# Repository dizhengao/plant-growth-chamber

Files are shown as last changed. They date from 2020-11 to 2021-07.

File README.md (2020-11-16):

# Plant Growth Chamber
[Link](https://www.hackster.io/biomaker-2019-team-8/ctod-from-cells-to-droplets-2b3b4f 'this is not yet the link to plant-chamber project') to hackster to be added here.
## Overview and Perspective
This project aims at building an automated plant growth chamber to grow and monitor *Arabidopsis thaliana* seedlings for plant research. The chamber will be equipped with following the features:

1. Provide a humidity, light and temperature-controlled environment which reach to **research level** - meaning that we aim at implementing it in real plant research and experiments conducted in given growth conditions are reproducible. 
2. **Real-time monitoring** of plant growth (camera +  humidity, light and temperature data) though Arduino WiFi module or Raspberry Pi.
3. Pumps for **auto-irrigation**. 
4. A **robotic arm** that can be used to perform some manual control remotely.
6. **Expandable** to larger scale and allow customable purposes. 
5. [Hopefully we can also develop a method to sow small *Arabidopsis* seeds automatically (maybe start with tobacco seeds which are larger!)]

The project will be based on 3D printing, Arduino (maybe together with Raspberry Pi), robotic arm and more.

### Motivation
*Arabidopsis thaliana* is model plant species widely used in plant research. The labor that has been put into growing and taking caring of those plants by researchers all over the world is unimaginable. We propose that simple automation designs could greatly speed up this processes and save researchers' time. [How automation can help xxx]

>TODO: High-throughput screening of many arabidopsis on a plate. 

>TODO: Generalization to other purposes and other plant species.

### Previous designs
>TODO: Search previous designs on hackster websties and others 

### More ideas
Please check our Design folder to find out how our ideas develop and some interesting designs.

## Start
Idea started in mid 2020. Documentation started on 12.11.2020.
Real project has not started but will be soon (hopefully...).
## Folder Index
1. 3D: Files for the 3D printing parts.
2. Code: .ino files for Arduino.
3. Design: Ideas and graphs.
4. Application: application files for Biomaker challenge 2020 (this should not be included in the final github page).

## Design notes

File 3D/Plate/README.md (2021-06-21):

3D print files for the 24-well plates and components of container.

List of items:

1. 24-well-plate: the plate for growing Arabidopsis seedlings
2. Tamp: a tamp to press soil
3. Container: the container for sealing the plate for CF imaging
4. Door: the door of the container for easily moving plates. Together with a bar.

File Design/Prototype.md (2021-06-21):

# Prototype

This file is a general design of the chamber.

- [Prototype](#prototype)
  - [1. Overview](#1-overview)
  - [2. Chamber](#2-chamber)
    - [2.1. Dimensions (cm)](#21-dimensions-cm)
    - [2.2. Growth Conditions](#22-growth-conditions)
    - [2.3. Sensor placement](#23-sensor-placement)
  - [3. Sensors](#3-sensors)
    - [3.1. Temperature-humidity Sensor](#31-temperature-humidity-sensor)
      - [3.1.1. Seeed Temperature, humidity, pressure, gas sensor](#311-seeed-temperature-humidity-pressure-gas-sensor)
      - [3.1.2. Temperature-only sensor](#312-temperature-only-sensor)
    - [3.2. Light Sensor](#32-light-sensor)
    - [3.3. Data collection](#33-data-collection)
    - [3.4. LCD display](#34-lcd-display)
    - [3.5. Camera](#35-camera)
  - [4. Control](#4-control)
    - [4.1. Temperature control](#41-temperature-control)
    - [4.2. Light](#42-light)
  - [5. Data logging and visualisation](#5-data-logging-and-visualisation)

## 1. Overview

1. Box (box + plate for plants + lamp + fan + mount)
2. sensor (circut + data log)
3. Enviortnment Control (Temp + Light + humidity + irrigation).
4. WiFi module
5. Cloud (website (heroku or github page or something)) and visulasition  
6. Robotic arm
7. [Thermal cameras](http://plantphenotyping.com/products/plantscreen-imaging-sensors/#fluorcam)
8. [Fluorescence cameras](http://plantphenotyping.com/products/plantscreen-imaging-sensors/#fluorcam) for in-box CF imaging.

## 2. Chamber

### 2.1. Dimensions (cm)

| Plant growing board    | Arduino board        | Raspberry Pi          | 4D touch screen | Raspberry Pi Screen |
| ---------------------- | -------------------- | --------------------- | --------------- | ------------------- |
| $12\times7.3\times1.8$ | $16\times7.5\times3$ | $8.5\times5.5\times2$ | $9\times5$      |                     |

### 2.2. Growth Conditions

Temperature: 20-22oC  
Humidity: 60%  
Light intensity: 6000 Lum or 150-200 PPFD (Photosynthetic Photon Flux Density).  

### 2.3. Sensor placement

Light sensor: near the growing board facing upward
Temperature sensor: on the wall
Humidity sensor: on the wall (how do we tell if the plant needs to be watered)

Camera: on the top of the chamber

Water pump: where to put it???

## 3. Sensors

### 3.1. Temperature-humidity Sensor

#### 3.1.1. Seeed Temperature, humidity, pressure, gas sensor

Check out xxx <mark> (add linke to .ino here).

#### 3.1.2. Temperature-only sensor

| Sensor Type| In XOD Library? | Physics(reading to Temp value)| Data Type |   Data Logging Method|
| ---------- | --------- | -------- | -------- | ----------- |
| NTC thermistors    | NO       |   [Steinhart-Hart equation](https://learn.adafruit.com/thermistor/using-a-thermistor) | Analog     | TBD|

| Sensor Type| In XOD Library? | Physics(reading to Temp value)| Data Type |   Data Logging Method|
| ---------- | --------- | -------- | -------- | ----------- |
| LM75   | Yes (download library from bio-maker tutorial)       |   Read directly through I2C bus | Digital | TBD|

The two sensors agree with each other

### 3.2. Light Sensor

| Sensor Type| In XOD Library? | Physics(reading to Temp value)| Data Type |   Data Logging Method|
| ---------- | --------- | -------- | -------- | ----------- |
|GL5528 photoresistor| NO      |  TBD  | Analog | TBD|

Analog sensor of low quality. Only roughly tells if the lights are bright enough. Can not be used for precise measurement.

### 3.3. Data collection

Check out ThingSpeak(https://thingspeak.com) and some examples (https://community.thingspeak.com/tag/raspberry-pi/)
Not accurate and can not tell humidity. 

### 3.4. LCD display

Address should be 20h (or 0x20), the document provided by the biomarker website is wrong.

### 3.5. Camera

See full instruction on how to set up [Raspberry pi camera](../Code/Camera/instruction-PiCamera.md) or [webcam](../Code/Camera/instruction-Webcam.md) through USB. Live stream can be viewed on adafruit IO's [feed](https://io.adafruit.com/Deebug/feeds/pi-camera) page.

## 4. Control

### 4.1. Temperature control

Large polystyrene box +
[Heating elements](https://uk.rs-online.com/web/p/heating-elements/2995950/), [air circulation Fan](https://uk.rs-online.com/web/p/axial-fans/6688827/), [cooling fan](https://www.banggood.com/Geekcreit-12V-6A-DIY-Electronic-Semiconductor-Refrigerator-Radiator-Cooling-Equipment-p-1074404.html?akmClientCountry=CN&cur_warehouse=CN), insulation panel

### 4.2. Light

LED panels from Photon (Czech):
- [LED Fyto-Panels from Photon](http://led-growing-lights.com/products/led-fyto-panels/#downloads) - Very expensive
- [Compact LED Bars](http://led-growing-lights.com/products/led-bars/compact-led-bars/#details)- Very expensive. 
  - PPFD: max. 920 µmol.m-2.s-1 (at the distance of 50 cm)
  - Light source: 12 x 126 pcs. LED 5,700 K cool white
  - Compact LED Bars ( stand-alone system with standard powering option) 2,690 €
- [LED Lights SL 3500](http://led-growing-lights.com/products/led-lights-sl-3500/): The one used in Wanne's lab.
  - 20x20 cm RGB. Light emitting diodes (LEDs): 455 nm, 530 nm, 617 nm, cool white (4,500 - 10,000 K) and others
  -  High light output - up to 3,000 µmol.m-2.s-1 at the distance of 20 cm
  - £4,500 with a controller

## 5. Data logging and visualisation

Connect Arduino to Rpi, and use Rpi to upload data to a Adafruit-IO or use Heroku.

Also display on a LCD screen.

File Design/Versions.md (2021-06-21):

# Versions

This file is a summary of different chamber versions.

## Version 1

### Time

Apr - Jun 2021

### Features

1. Temperature, humidity and pressure data logged to Adafruit (real-time monitoring) and Google drive (long-term storage and data analysis)
2. Low-resolution images taken every 30s for Adafruit (real-time monitoring) and high-resolution images taken every 30min for Google drive (long-term storage and data analysis)
3. Auto-irrigation every 48 h (Changed to 60 h later)

A 14-day trial was done from 27.4.21 to 10.5.21. Refer to [Trials](../Trials/Trials.md) for more information.

### Images

Refer to Pictures/Box/Version1 and Pictures/Circuit/Version1

## Version 2

### Time

17th Jun - xxx 

### Expectation

0. [x] Clean layout.
1. Temperature and humidity control.
2. Sufficient (and adjustable) light source.
3. Programmable light switch.

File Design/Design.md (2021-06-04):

# Design

This file summaries general design ideas and resources to build the project.

- [Design](#design)
  - [1. Ideas](#1-ideas)
  - [2. Questions](#2-questions)
  - [3. Reference](#3-reference)
    - [3.1. General](#31-general)
    - [3.2. Suppliers](#32-suppliers)
    - [3.3. Some Hackster projects](#33-some-hackster-projects)
    - [3.4. Hardware](#34-hardware)
      - [3.4.1. Relay](#341-relay)
      - [3.4.2. WiFi](#342-wifi)
      - [3.4.3. 4D Systems programmable touchscreen](#343-4d-systems-programmable-touchscreen)
    - [3.5. Software-Arduino IDE](#35-software-arduino-ide)
    - [3.6. Software-3D printing](#36-software-3d-printing)
    - [3.7. Software-XOD](#37-software-xod)
      - [3.7.1. XOD libraries for Open-Smart Rich UNO R3](#371-xod-libraries-for-open-smart-rich-uno-r3)
      - [3.7.2. Basic XOD elements](#372-basic-xod-elements)
    - [3.8. Other references](#38-other-references)
    - [3.9. Arduino-Rpi communication](#39-arduino-rpi-communication)
    - [3.10. Raspberry pi](#310-raspberry-pi)
  - [4. Knowledge](#4-knowledge)
    - [4.1. Electrical Sensors](#41-electrical-sensors)
    - [4.2. WiFi modules](#42-wifi-modules)
    - [4.3. Programming on Hardware](#43-programming-on-hardware)
    - [4.4. DIY](#44-diy)
  - [5. Papers](#5-papers)

## 1. Ideas

quick thoughts can be added here

[20210420-JMH] 1. To test watering system, fill plates with soil and see the change of soil color from camera. 2. Firmly press the soil by printing a 'presser' with the same dimensions as plates. 3. Whether use compost only or with vermiculite.

[20200303-ZD] Thermo cameras and fluorescence cameras. Also check out devices on [Photon](https://handheld.psi.cz/).

[20201203-ZD] To have another raspberry Pi with screen showing real time images and data logs, which can be put in home/lab bench so that you won't even have to have a computer to do the monitoring. It would be great if we have this along side with our prototype at the showcase event.

[20201125-Che] Lamp: Control RGB light separately; create different light intensity and RGB components for different experimental purposes.

[20201123-JMH] 1. Use robotic arm or something else to spray water from the top. This will be especially useful to water individual wells that are dried as a complement of watering from the bottom. 2. May include lime as CO2 scrubber to customize CO2 concentration for experiment purposes.

[20201115-ZD] Expand the prototype to larger scale: Use a robot with a camera to move around and take pictures of plants every xx minutes/hours; or install tracks for camera on the top of the chamber to take images every xx minute/hour.

## 2. Questions

*Mar 21*

1. [x] How to connect Arduino to Rpi, and use Rpi to upload data to a cloud?

*Feb 21 - sadly we no longer use XOD*

1. [x] How to search XOD nodes? 
2. [x] How to create our own nodes? And how hard/easy is this?
3. [x] Devices using I2C protocol- How to find out their address? Does each of device come with different address or we can customize the address?
4. [x] What is DONE used for on XOD?

## 3. Reference

### 3.1. General

[Letusgrow](https://www.lettusgrow.com)  
[Growcab](https://wikifactory.com/+growcab/growcab)

### 3.2. Suppliers

- [RS](https://uk.rs-online.com/web/)
- https://thepihut.com/
- https://shop.sb-components.co.uk/collections/raspberry-pi
- https://shop.pimoroni.com/
- https://www.okdo.com/
- https://uk.farnell.com/?pf_custSiteRedirect=true
- https://www.thorlabs.com/

### 3.3. Some Hackster projects

- :star:[FytoScope Chamber FS 130](http://growth-chambers.com/products/small-fytoscopes/fytoscope-chamber-130/#details) from Photon
- [Biomaker Tutorial](https://www.hackster.io/159756/biomaker-tutorial-1-getting-started-4fc966)
- :star:[Lunaflow](https://www.hackster.io/lunaflow/lunaflow-bioluminescent-plankton-for-3d-flow-visualisation-d60cbe): incubator design, **temperature control**, real-time monitor camera, codes.
- [Variable-Time Camera for Monitoring Plant Pollination Events](https://www.hackster.io/team-ppi/variable-time-camera-for-monitoring-plant-pollination-events-ad21e7) A **video and time-lapse monitor** to record pollinators interacting with plants. This project included an environmental sensor to measure temperature, humidity and barometric pressure and wrote this data into the image file names for later analysis.
- [Biofab Incubator](https://www.hackster.io/170194/biofab-incubator-6f5b0e) A low cost programmable incubator for growing mycelium textile. This project uses sensors to measure temperature and humidity and feeds this information back into the system to maintain constant environmental conditions.- [eCO-SENSE](https://www.hackster.io/glen-chua/eco-sense-soil-sensors-powered-by-plant-photosynthesis-be80a2) A sensor to monitor soil conditions powered by plant growth. This project uses a temperature sensor, moisture sensor and gas sensor to take measurements of soil 68 conditions and adds a bluetooth module to send the data wirelessly to a phone or computer.
- [Low Cost Oxygen Sensor for Bioreactors](https://www.hackster.io/biomaker/low-cost-oxygen-sensor-for-bioreactors-c7e066) This project developed a custom low-cost oxygen sensor to measure oxygen levels in cultures of E. coli, and logged the data via an Arduino microcontroller. 
- [A Behavioural Chamber to Evaluate Rodent Forelimb Grasping](https://www.hackster.io/alejandrocarn/a-behavioural-chamber-to-evaluate-rodent-forelimb-grasping-bedb1a) This project uses a light emitter and light sensor to monitor when a rodent moves past a certain threshold, and triggers release of a sugar pellet when it does. 

Refer to some plant growth products and facility that have been using in real plant research (e.g. in PGF) and [gardin](https://gard.in/) (This is very expensive so probably we won't use them in our project.)

### 3.4. Hardware

#### 3.4.1. Relay

- [Connecting a 12v 8 Channel Relay to an External Power Supply and RaspberryPi](https://medium.com/@jinky32/connecting-a-12v-8-channel-relay-to-an-external-power-supply-and-raspberrypi-6fec119c112c)  
- [Control High Voltage Devices with Arduino](https://howtomechatronics.com/tutorials/arduino/control-high-voltage-devices-arduino-relay-tutorial/)

#### 3.4.2. WiFi

Arduino there are some modules based on the [ESP8266 microchip](https://en.wikipedia.org/wiki/ESP8266) such as Adafruit Feather HUZZAH (I have this!, read manual [here](https://learn.adafruit.com/adafruit-feather-huzzah-esp8266)) or [SparkFun ESP8266 Thing Dev Board](learn.sparkfun.com/tutorials/esp8266-thing-development-board-hookup-guide).

#### 3.4.3. 4D Systems programmable touchscreen

[spec sheet](https://static1.squarespace.com/static/584d41b3f5e2310b396cd953/t/5ba376490e2e7299a6f96506/1537439314392/gen4-uLCD-32D_datasheet_R_1_5.pdf), [Introduction](https://static1.squarespace.com/static/584d41b3f5e2310b396cd953/t/5ba374cac2241b80e970e46f/1537438935415/Visi-Genie_userguide_R_2_0.pdf)

### 3.5. Software-Arduino IDE

Add resources here.

### 3.6. Software-3D printing

Add resources here.

### 3.7. Software-XOD

#### 3.7.1. XOD libraries for Open-Smart Rich UNO R3

- Real time clock module: datetime (https://xod.io/libs/xod/datetime/) and ds-rtc (https://xod.io/libs/xod- dev/ds-rtc/) libraries.
- Onboard LM75 temperature sensor: lm75a-temp-sensor node can be found in the gst/lm75atempsensor XOD library.
- Onboard 4-digit display: tm1637-dev node from the cesars/tm1637 or cesars/tm1637-v2 library. This library also contains other nodes for onboard display, such as tm1637-decex, tm1637-autorange, tm1637-digits (for string)
- Various onboard modules: cesars/rich-uno-r3, cesars/utils (contains nodes required by the her other libraries)
- sd-log node: from xod/commonhardware library, for saving data into SD card.
- OLED screen: wayland/ssd1306-oled-i2c library. Nodes: ssd1306-oled-i2c-device
- gweimer/utils

#### 3.7.2. Basic XOD elements

- Format number: *format-number* node
- *join* node

### 3.8. Other references

- [Robotic arm](https://shop.pimoroni.com/products/mearm-robot-raspberry-pi-kit?variant=21775370223699&currency=GBP&utm_source=google&utm_medium=cpc&utm_campaign=google+shopping?utm_source=google&utm_medium=surfaces&utm_campaign=shopping&gclid=Cj0KCQiA48j9BRC-ARIsAMQu3WTvhcmb-bZv5fxLHJMAYPL-1Bl-ShvdAIO8ML_nc9I4GpWhqUfcmDkaAn6uEALw_wcB), [Makeblock robot](https://www.makeblock.com/cn/mbot/)
- https://www.nature.com/articles/d41586-019-01590-z
- [Open-source lab](https://www.appropedia.org/Open-source_Lab)
- [BENEFICIAL BIO](https://beneficial.bio/)
- [Photon-plant phenotyping systems](http://plantphenotyping.com/)

### 3.9. Arduino-Rpi communication

An introduction [article](https://roboticsbackend.com/raspberry-pi-arduino-serial-communication/).

Python packages: [pySerial API](https://pyserial.readthedocs.io/en/latest/pyserial_api.html)

On Arduino side: [UART](https://www.arduino.cc/reference/en/language/functions/communication/serial/)

### 3.10. Raspberry pi

- [Pi Camera](https://projects.raspberrypi.org/en/projects/getting-started-with-picamera/4) control with Python.
- Live stream with [USB webcam on local browser](https://tutorials-raspberrypi.com/raspberry-pi-security-camera-livestream-setup/) or with [pi-camera](https://learn.adafruit.com/cloud-cam-connected-raspberry-pi-security-camera/adafruit-io), [pi-camera using motion](https://learn.adafruit.com/cloud-cam-connected-raspberry-pi-security-camera?view=all). Also see this for a wayaround 
- [rsync](https://www.raspberrypi.org/documentation/remote-access/ssh/rsync.md)
- [Servo moter](https://learn.adafruit.com/adafruits-raspberry-pi-lesson-8-using-a-servo-motor)
- [Power Control](https://learn.adafruit.com/adafruits-raspberry-pi-lesson-13-power-control)

## 4. Knowledge

### 4.1. Electrical Sensors

Che wrote:

- How do we communicate with sensors? clock
- How we process the data reading from sensors?
- Data log and plots.
- Initializing and calibration. [ZD] Temp: using a thermometer; Light intensity: ZD can borrow a professional one from lab; humidity: buy a professional one from Amazon?
- Camera-> [ZD] There are many camera modules for Raspberry Pi but not as many for Arduino (as far as I know...). So (1) use Raspberry Pi (2) search for more Arduino projects with camera; (3) search for adapters to connect Arduino and Raspberry Pi cameras.

### 4.2. WiFi modules

Che wrote:

- How do we achieve remote control and communication through WiFi? ->[ZD] For Raspberry Pi it is very straightforward as it has built-in WiFi module, for Arduino there are some modules based on the [ESP8266 microchip](https://en.wikipedia.org/wiki/ESP8266) such as Adafruit Feather HUZZAH (I have this!, read manual [here](https://learn.adafruit.com/adafruit-feather-huzzah-esp8266)) or [SparkFun ESP8266 Thing Dev Board](learn.sparkfun.com/tutorials/esp8266-thing-development-board-hookup-guide).

### 4.3. Programming on Hardware

Che wrote:

- Syntax of the programming language;
- Debug and tests scheme.
- Development tools.

### 4.4. DIY

ZD:

- chamber (Should have enough insulation for heat)
- plates for growing Arabidopsis
- scaffolds to mount sensors

Che wrote:

- 3D printing and CAD models.
- Robotic arms

## 5. Papers

1. Jolles, J. Broad-scale Applications of the Raspberry Pi: A Review and Guide for Biologists. https://ecoevorxiv.org/qh9sz/ (2021) doi:10.32942/osf.io/qh9sz.
1. Tausen, M. et al. Greenotyper: Image-Based Plant Phenotyping Using Distributed Computing and Deep Learning. Front. Plant Sci. 11, (2020).
1. Gaggion, N. et al. ChronoRoot: High-throughput phenotyping by deep segmentation networks reveals novel temporal parameters of plant root system architecture. bioRxiv 2020.10.27.350553 (2020) doi:10.1101/2020.10.27.350553.

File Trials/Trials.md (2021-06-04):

Trials/27.4# Trials

## 1st trial: 27.4.21-10.5.21

### Summary

This is our first trial aiming to test some basic features before moving forward, starting from 11am 27.4.21 and lasted for 14 days. This is the first version of box and 24-well plate, with no environment controls and low brightness light. 1 Pai choi seed was sown per well.

#### Features

1. Temperature, humidity, pressure data were pushed to Adafruit-IO every 30s for real-time monitoring and saved to Google drive for long-term storage.
2. Low-resolution images were taken every 30s and pushed to Adafruit for real-time monitoring. High-resolution images were taken every 30min and saved to Google drive for long-term storage and data analysis.
3. Auto-irrigation every 48 h (Changed to 60 h later).

#### Problems

0. Error logs can be found in the working directory. Some general problems are summaries below.
1. Program was interrupted many times because of Internet connection failure. -> Separate local data logging and data upload into two parallel program will solve this.
4. Temperature in the chamber is high when light is on (Compare NTC values and LM75 values). -> Temperature control features will take care of this.
5. Humidity in the chamber is low when light is on. -> Humidity control features will take care of this.
6. Too much water during auto-irrigation, and water cannot drain away. Changed irrigation intervals to 60h. Need to reduce watering time from 30s to 15s (or 10s) next time. -> Irrigation calibration will take care of this.
7. Light intensity was not enough.

Some error logs

2. 2021/04/28 11:33:04AM: Sensors data interrupted (unknown reasons...) but images were taken and uploaded as normal. Restarted Rpi and re-located the box to kitchen at 22.15.
3. 2021/04/30 12pm: Sensors data interrupted (unknown reasons...) but images were taken and uploaded as normal. Restarted Rpi.

### Improvement and upcoming features

1. Separate local data logging process and data upload process into two parallel program will be able to disentangle local data logging from any Internet connection problems, ensuring that data is not lost when Internet is down.
2. Temperature and humidity control features will be implemented in the next version.
3. Calibrate irrigation intervals, duration and make a hole at the bottom of the container to drain redundant water.
4. Use a brighter light source.

### Images

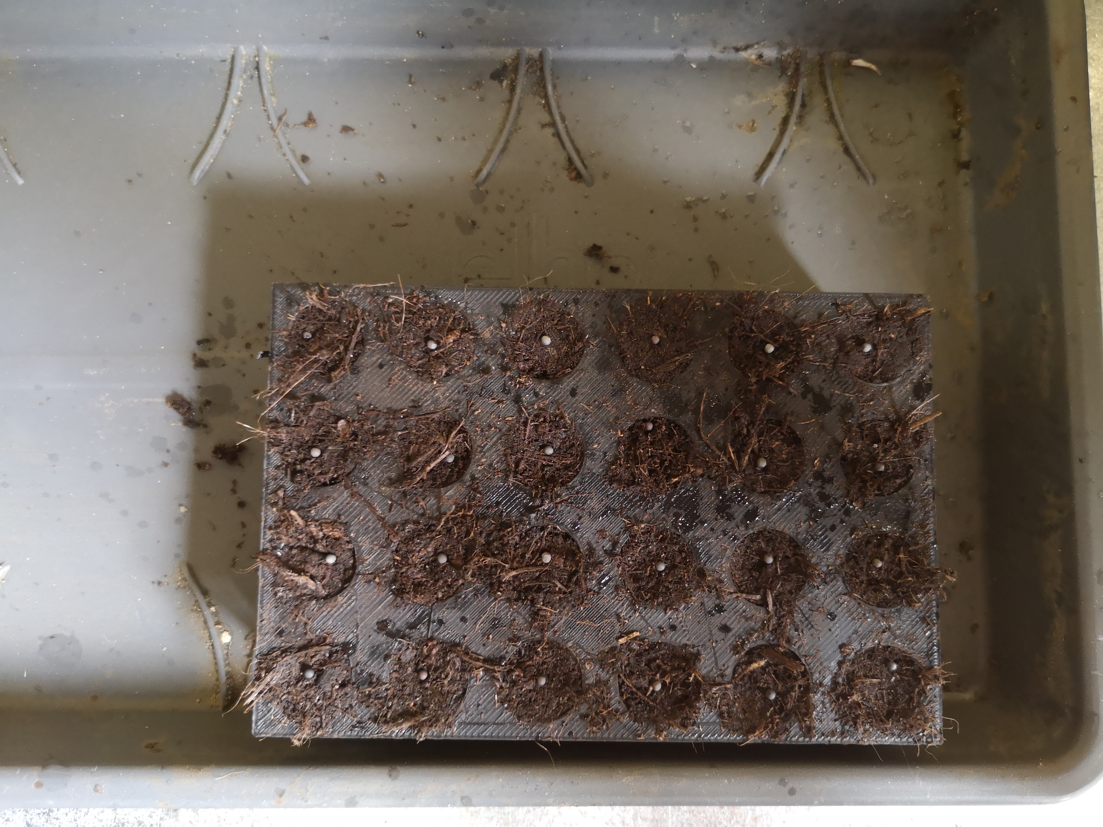
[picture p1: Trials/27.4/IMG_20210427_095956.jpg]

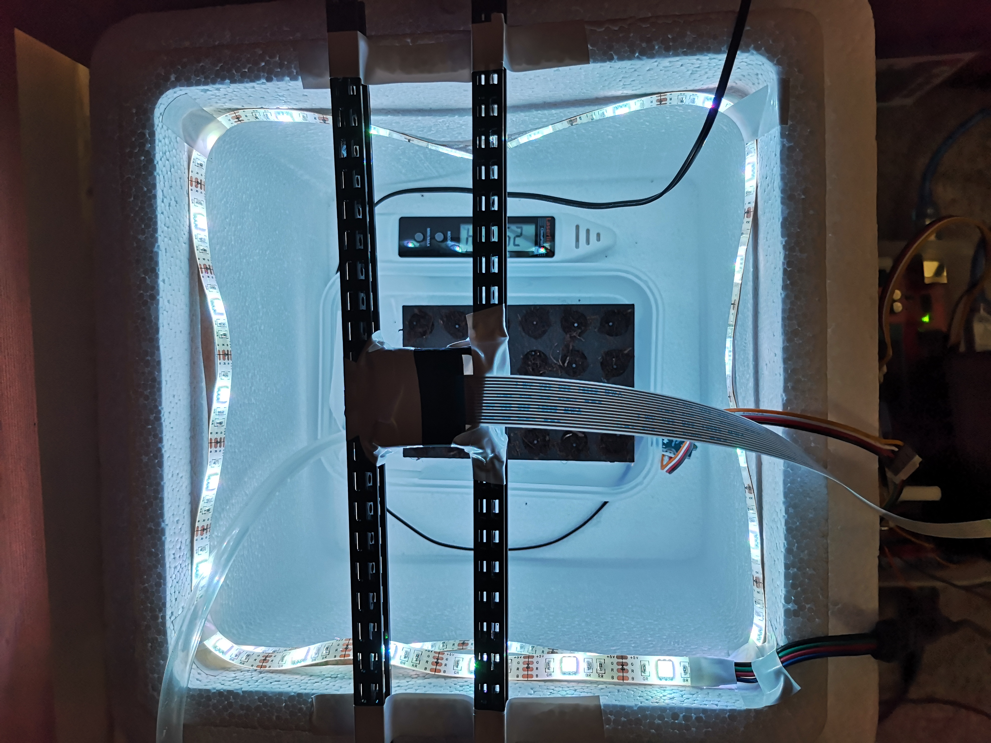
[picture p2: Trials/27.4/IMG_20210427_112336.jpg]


### Results

Environmental data during the 14-day trial is shown below. The environment will be more controlled in our next version.
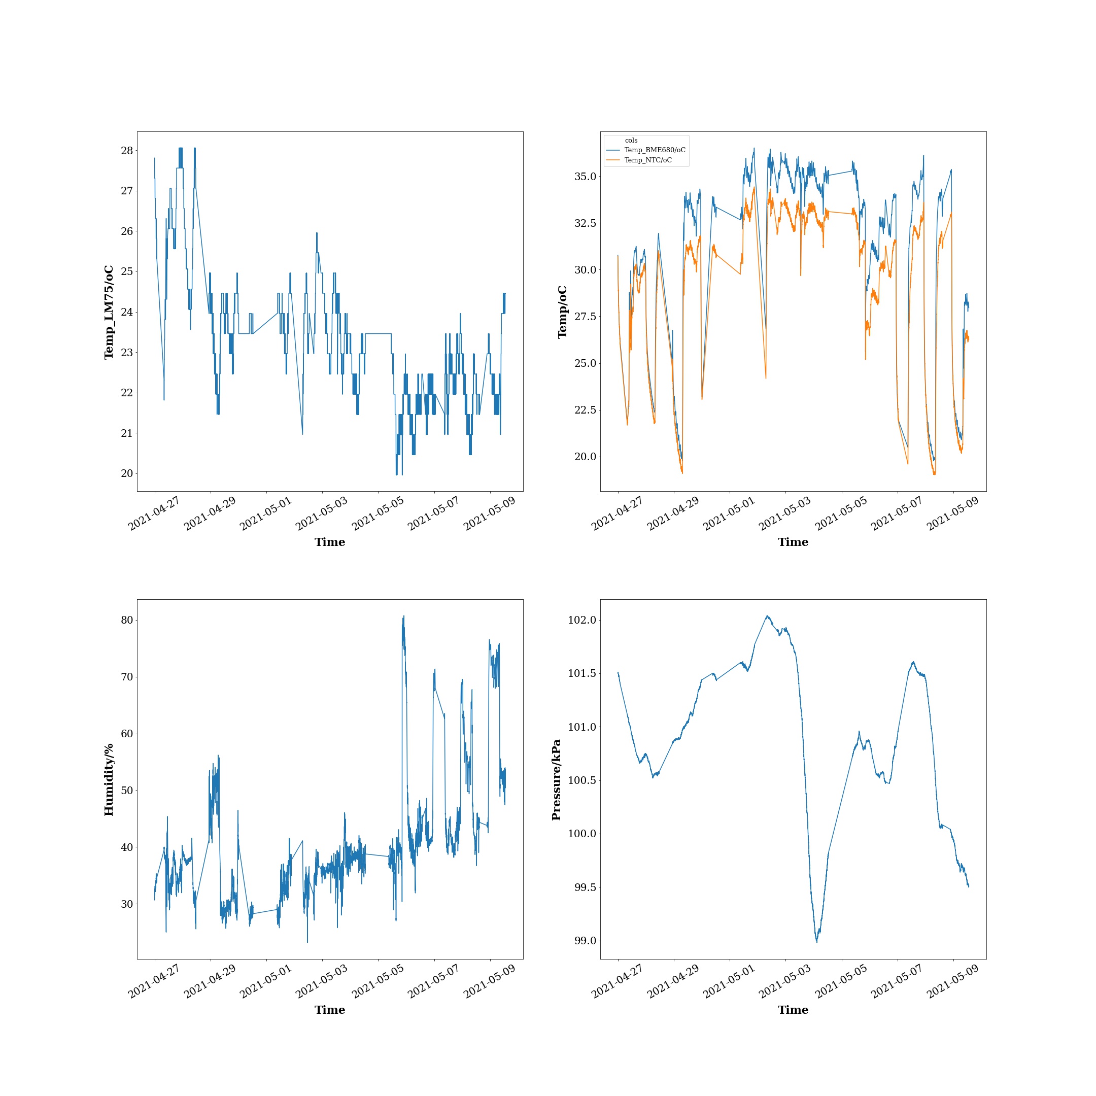
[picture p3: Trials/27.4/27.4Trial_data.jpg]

>Plot legend: Temperature, humidity and pressure data during the first trial. Top left: Temperature outside of the box. Top right: Temperature within the box measured by two different sensors. Bottom left: Relative humidity within the box. Bottom right: Air pressure within the box.

A [time-lapse video ](https://youtu.be/F5084XwlkN0) was made from high-resolution images taken by Raspberry Pi.

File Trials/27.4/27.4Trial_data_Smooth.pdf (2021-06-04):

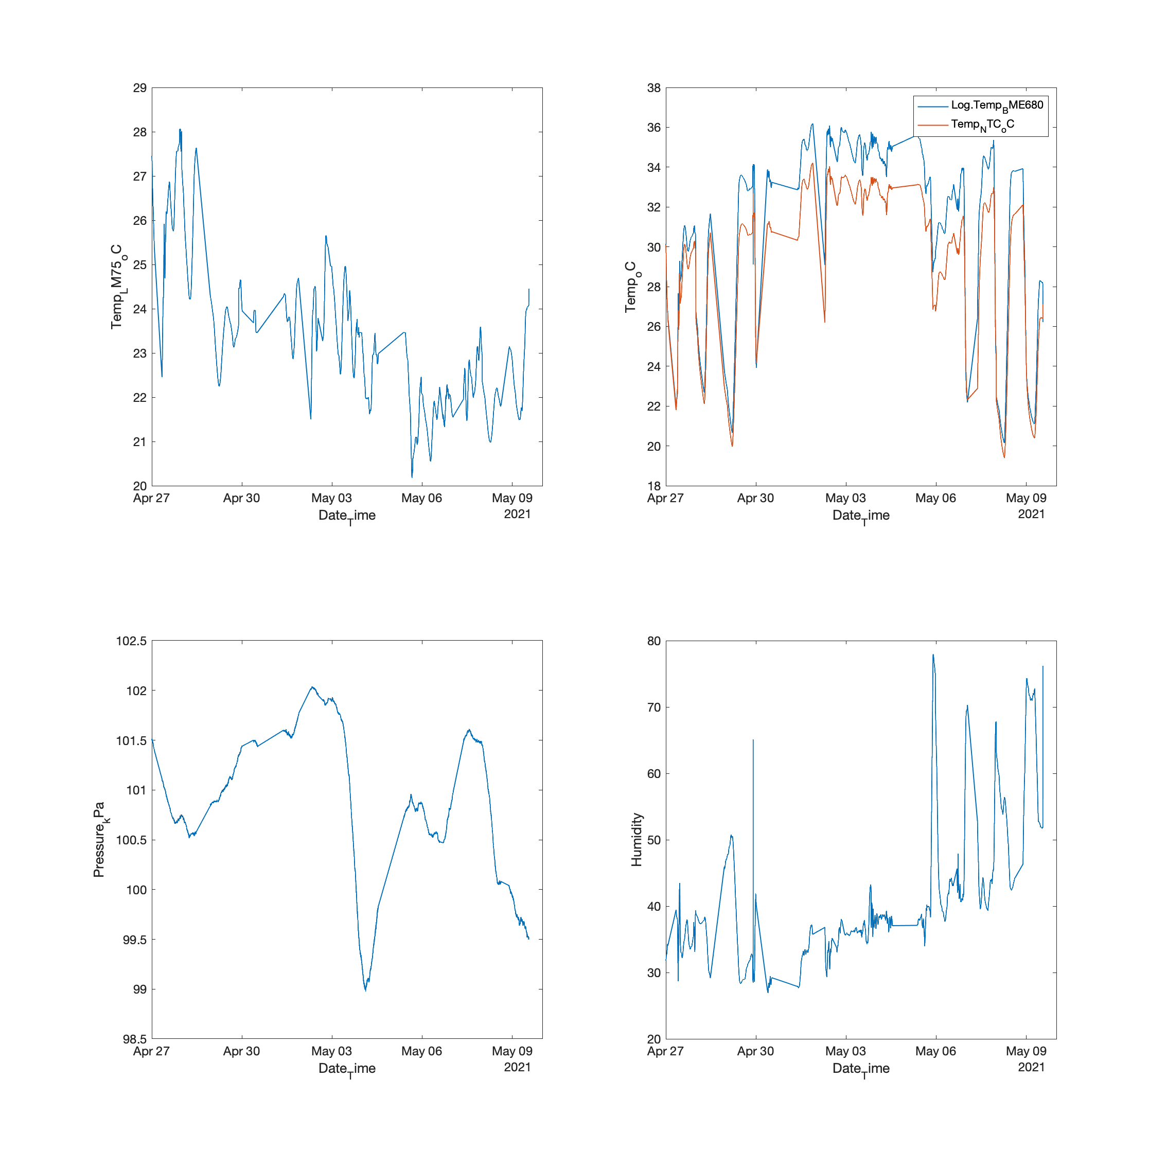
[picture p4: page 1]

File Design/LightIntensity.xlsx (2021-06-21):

Distance/cm | PPFD | Notes
10 | 3000 | Full Beam. Measured on 12.6.21 by LI6800. The light was held by hand so these are just rough numbers
15 | 1700
20 | 1100
25 | 700
30 | 550

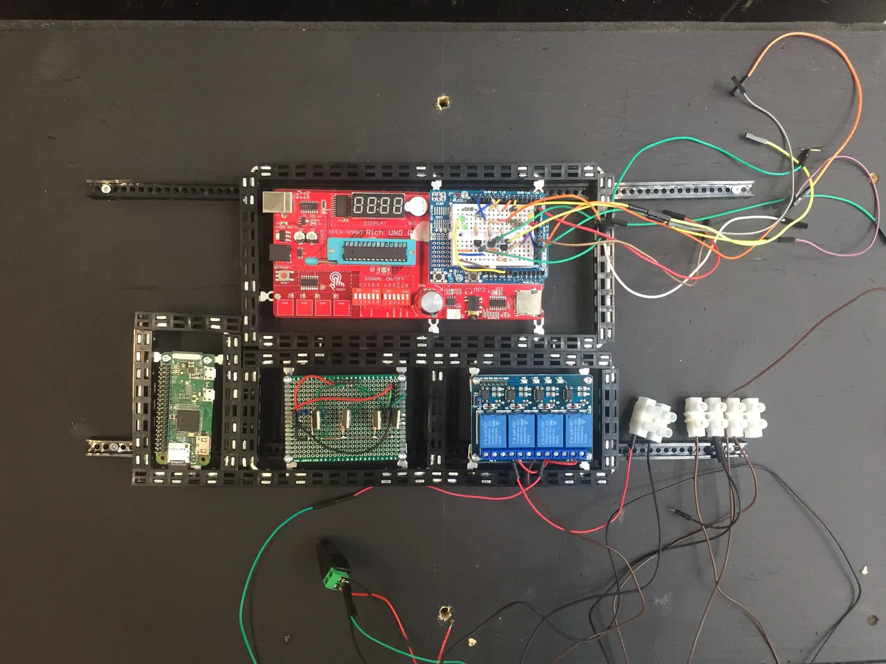
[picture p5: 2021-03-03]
Pictures/ref-mounted-electronics.jpg

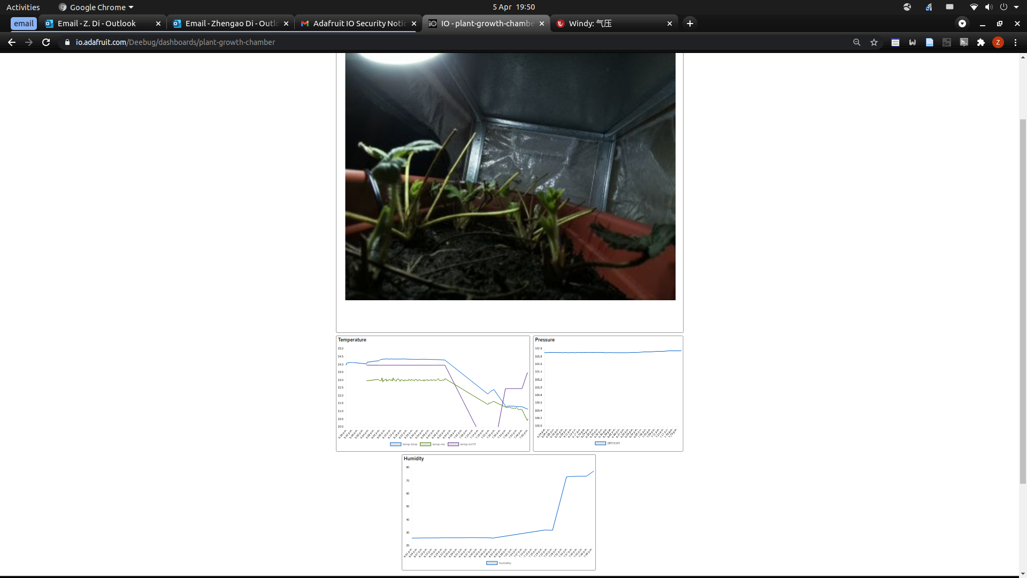
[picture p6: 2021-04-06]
Pictures/Screenshot from 2021-04-05 19-50-20.png

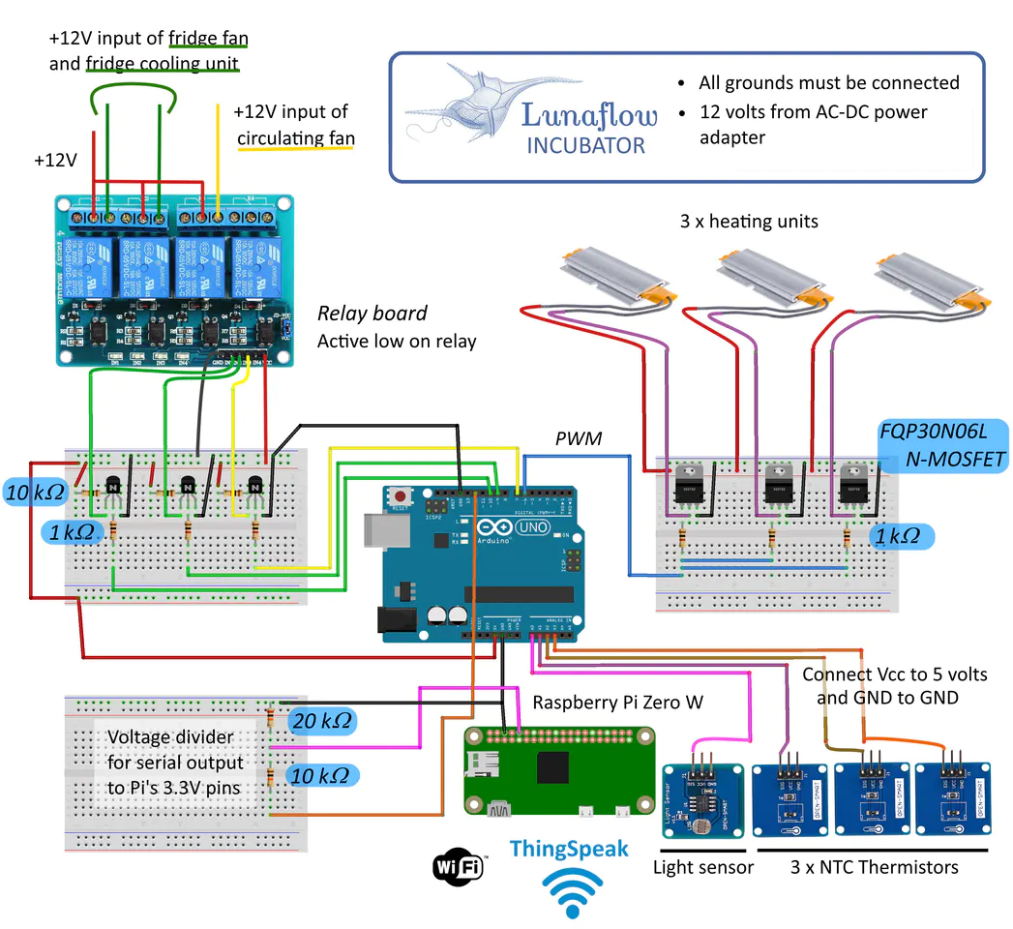
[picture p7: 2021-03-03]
Pictures/Ref-incubator-circuit.jpg

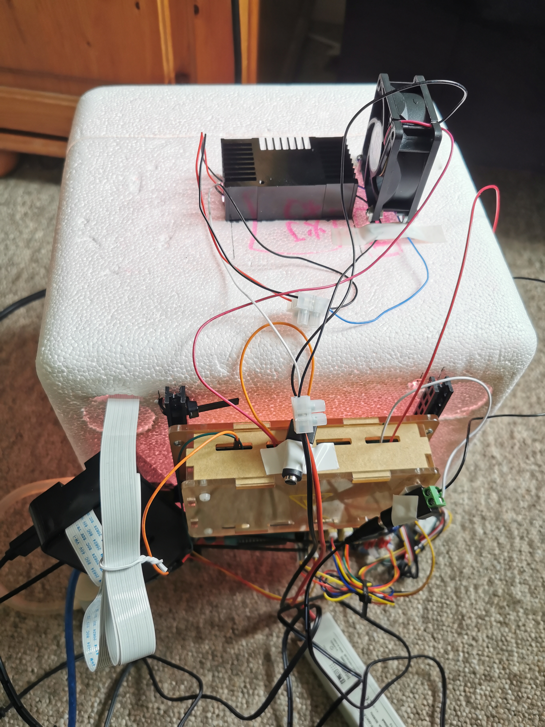
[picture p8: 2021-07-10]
Pictures/Box/Version2/Box2.0(Back_new).jpeg

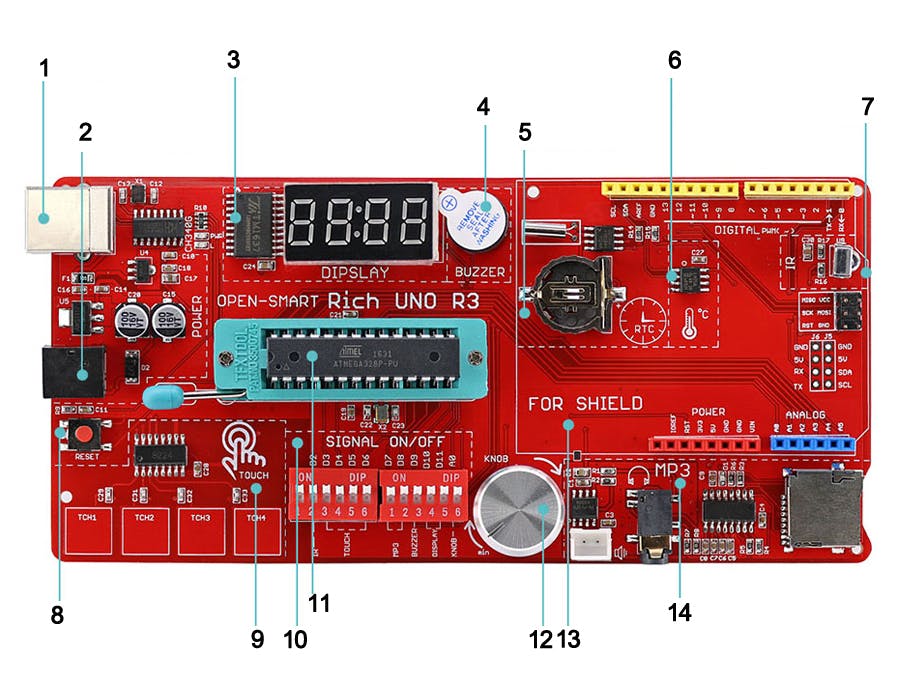
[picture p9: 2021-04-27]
Pictures/Rich UNO R3 multifunction board.jpg

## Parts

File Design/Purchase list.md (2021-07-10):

# Shopping list

- [Shopping list](#shopping-list)
  - [1. Ideas](#1-ideas)
  - [2. 已购](#2-已购)
  - [3. To Buy](#3-to-buy)
  - [- [ ] Cooler?](#----cooler)
  - [Light](#light)
  - [Supplier](#supplier)

Code PDGU.EZZZ

## 1. Ideas

- [Jumper Wire](https://uk.rs-online.com/web/p/breadboard-jumper-wire/5053396/)
- [Light](https://uk.rs-online.com/web/p/led-strip-lights/9125016/): Need 6000 lumens. Check out [LED Kits](https://uk.rs-online.com/web/c/displays-optoelectronics/led-lighting-system-components/led-kits/?sort-by=Application&sort-order=desc&pn=1) from RS
- An all-in-one sensor [Enviro](https://shop.pimoroni.com/products/enviro?variant=31155658489939)
- Lamp: [Ali](https://www.aliexpress.com/item/4001095381063.html), [Rpi](https://tutorials-raspberrypi.com/connect-control-raspberry-pi-ws2812-rgb-led-strips/), [PPF and Lumen](https://www.waveformlighting.com/horticulture/convert-ppf-to-lumens-online-calculator)
- [Fan](https://thepihut.com/products/miniature-5v-cooling-fan-for-raspberry-pi-and-other-computers?_pos=2&_sid=7ba767831&_ss=r)
- [Water Pump](https://thepihut.com/products/peristaltic-liquid-pump-with-silicone-tubing-5v-to-6v-dc-power?_pos=5&_sid=7ba767831&_ss=r), https://uk.rs-online.com/web/p/water-pumps/9146944/
- IoT kit https://www.sparkfun.com/products/14682

This webpage contains useful information about integrated sensors for RaspberryPi: [RaspberryPi sensor list and tutorial](https://tutorials-raspberrypi.com/raspberry-pi-sensors-overview-50-important-components/)

## 2. 已购
0. [Pump](https://www.ebay.co.uk/itm/MINI-SUBMERSIBLE-WATER-PUMP-3V-to-6V-DC-AQUARIUM-arduino-UK-seller-BBC-micro/122508463023): DC Voltage:2.5-6V. Maximum lift:40-110cm. Flow rate:80-120L/H
1. **Two** Raspberry Pi 4 B 4GB, RS Stock No. 182-2096, https://uk.rs-online.com/web/p/raspberry-pi/1822096/
2. LCD Touch Screen with 7in Capacitive Touch Screen, RS Stock No. 899-7466, https://uk.rs-online.com/web/p/products/8997466/
3. Two Sandisk Storage Card 16Gb, RS Stock No. 121-3897, https://uk.rs-online.com/web/p/products/1213897/
4. Two Okdo Raspberry Pi Power Supply, USB Type C with Universal Plug Type, 1.5m, RS Stock No. 187-1381, https://uk.rs-online.com/web/p/products/1871381/
5. DesignSpark ABS Case, RS Stock No. 117-6025, https://uk.rs-online.com/web/p/products/1176025/
6. SAD-01, Breadboard Prototyping Board, RS Stock No. 453-8824, https://uk.rs-online.com/web/p/breadboards/4538824/
7. 1.75mm Black PLA 3D Printer Filament, 300g RS Stock No. 832-0406, https://uk.rs-online.com/web/p/3d-printing-materials/8320406/
8.  Raspberry Pi, Camera, RS Stock No. 913-2664, https://uk.rs-online.com/web/p/raspberry-pi-cameras/9132664/
9.  2* [heating element, RS Stock No. 299-5950](https://uk.rs-online.com/web/p/heating-elements/2995950/)
10. [Bostik Bond-Flex 100HMA Black Sealant Non-Slump Paste 300 ml Cartridge. RS Stock No. 341-0955](https://uk.rs-online.com/web/p/sealants/3410955/)
11. 3* [Seeed Studio 101020513, Grove-Temperature, Humidity, Pressure and Gas Sensor (BME680) for BME680 RS Stock No. 184-5086](https://uk.rs-online.com/web/p/sensor-development-tools/1845086/)
12. 2* [Raspberry Pi 1m HDMI to Micro HDMI Cable in Black. RS Stock No. 187-1377](https://uk.rs-online.com/web/p/raspberry-pi-cables/1871377/)
13. [Laserliner 082.034A Digital Hygrometer, RS Stock No. 191-9564](https://uk.rs-online.com/web/p/hygrometers/1919564/)
14. [Okdo ABS Case in Black. RS Stock No. 187-3799](https://uk.rs-online.com/web/p/raspberry-pi-cases/1873799/)
15. [Feather HUZZAH 3213](https://www.mouser.co.uk/ProductDetail/Adafruit/3213/?qs=AQlKX63v8RuWaQY9I2LOXA%3D%3D)
16. [RS PRO 1kΩ Carbon Film Resistor 2W ±5%. RS Stock No. 707-8861](https://uk.rs-online.com/web/p/through-hole-fixed-resistors/7078861/)
17. [RS PRO 10kΩ Carbon Film Resistor 2W ±5%, RS Stock No. 707-8906](https://uk.rs-online.com/web/p/products/7078906/)
18. [12 V dc, DC Axial Fan, 60 x 60 x 25mm, 39.1m³/h, 2.8W. RS Stock No. 668-8827](https://uk.rs-online.com/web/p/axial-fans/6688827/)
19. 3* [Sandisk Storage Card for Raspberry Pi, 16GB NOOBs RS Stock No.:121-3897](https://uk.rs-online.com/web/p/raspberry-pi-os/1213897/) 
20. [Samsung 32 GB MicroSDHC Card Class 10 RS Stock No. 144-9017](https://uk.rs-online.com/web/p/micro-sd-cards/1449017/)
21. [RS PRO 0.8MP 30fps Webcam, 1080 x 720 RS Stock No. 201-3517](https://uk.rs-online.com/web/p/products/2013517/) £66
22. [RS PRO Black Cable Tie Nylon, 300mm x 4.8 mm RS Stock No. 233-487](https://uk.rs-online.com/web/p/products/0233487/) £13.25
23. [Seeed Studio, Grove Base Shield V2 RS Stock No. 174-3233](https://uk.rs-online.com/web/p/products/174-3233/) £6.70
24. 5 * [Seeed Studio 110990210 for use with Grove-Base Shield RS Stock No. 179-3726](https://uk.rs-online.com/web/p/products/179-3726/) £2.54*5
25. [Seeed Studio, SPDT Relay - 103020133. RS Stock No. 184-5099](https://uk.rs-online.com/web/p/power-motor-robotics-development-tools/1845099) £9.06
26. 20* [N-Channel MOSFET, 33 A, 100 V, 3-Pin TO-220AB Infineon IRF540NPBF RS Stock No.: 914-8154](https://uk.rs-online.com/web/p/mosfets/9148154/) £12.28
27. [Clever Little Box, CLB Cable Mount DC Jack Socket, 1Pole 1A RS Stock No. 810-4605](https://uk.rs-online.com/web/p/jack-plugs-sockets/8104605/) £2.78
28. [XP Power,12V dc, 5W Plug In Power Supply, 420mA, Level VI Efficiency, 1 Output Switched Mode Power Supply, Type G RS Stock No. 121-7133](https://uk.rs-online.com/web/p/ac-dc-adapters/1217133/) £6.49
29. [ON Semiconductor ALS-GEVB, Ambient Light Sensor (ALS) Shield Evaluation Board Evaluation Board for NOA1305CUTAG,RS Stock No. 171-9122](https://uk.rs-online.com/web/p/sensor-development-tools/1719122/) £6.26
30. [brennenstuhl 3m 6 Socket Type G - British Extension Lead, 230 V RS Stock No. 768-5320 ](https://uk.rs-online.com/web/p/extension-leads-cable-reels/7685320/) £19.55
31. [RS PRO 1.75mm White PLA 3D Printer Filament, 1kg RS Stock No. 832-0223](https://uk.rs-online.com/web/p/3d-printing-materials/8320223/) £29.17
32. [RS PRO Silicone Heater Mat, 5 W, 50 x 100mm, 12 V dc RS Stock No. 245-528](https://uk.rs-online.com/web/p/heater-pads/0245528/) £22.21
33. [ILS ILK-PETUNIA-01 LED Light Kit, OSLON SSL Petunia RS Stock No.: 875-0037](https://uk.rs-online.com/web/p/led-kits/8750037/) £145.60
34. [RS PRO UK Mains Connector BS 1363, 13A, Cable Mount, 250 V ac RS Stock No. 854-380](https://uk.rs-online.com/web/p/mains-plugs-sockets/0854380/) £6.10
35. 10* [TE Connectivity 1776293-2 Terminal Strip, 30A, 250 V Screw Screw RS Stock No. 782-2857](https://uk.rs-online.com/web/p/standard-terminal-blocks/7822857?cm_mmc=UK-PLA-DS3A-_-google-_-CSS_UK_EN_Connectors_Whoop-_-Standard+Terminal+Blocks_Whoop+(2)-_-7822857&matchtype=&aud-826607888547:pla-302090786601&gclid=Cj0KCQjwyZmEBhCpARIsALIzmnLCHxAQ4jYSvQ67LUSVpl-s1F3SjJgTcXCgc59uX36_UIUZsUNBkCMaAnZYEALw_wcB&gclsrc=aw.ds) £1.68 * 10
37. [HellermannTyton Adhesive Lined Heat Shrink Tubing, Black 4mm Sleeve Dia. x 1.2m Length 4:1 Ratio, TA42 Series RS Stock No. 914-6802](https://uk.rs-online.com/web/p/heat-shrink-cold-shrink-sleeves/9146802/) £4.45
38. [Sandisk Micro SD Card 128 GB MicroSDXC Card Class 10, UHS-1 U1 RS Stock No.: 174-7340](https://uk.rs-online.com/web/p/micro-sd-cards/1747340) £69.34
39. [RS PRO RS41 K Input Wired Digital Thermometer RS Stock No. 123-1940](https://uk.rs-online.com/web/p/products/1231940/) £47.18
40. [RS PRO Digital Timer Switch 230 V ac 100h RS Stock No. 178-5368](https://uk.rs-online.com/web/p/time-switches/1785368/) £18.56
41. [RS PRO, 24 V dc, DC Axial Fan, 80 x 80 x 25mm, 68m³/h, 2.4W RS Stock No. 668-8833](https://uk.rs-online.com/web/p/axial-fans/6688833/) £9.72
42. [Fan Filter, Fan Mounted 86.5 x 86.5mm, for 80mm Fan PET RS Stock No. 221-336](https://uk.rs-online.com/web/p/fan-filters/0221336/) £5.82
43. [RS PRO, 20W Plug In Power Supply 24V ac, 800mA Type G RS Stock No. 139-1777 ](https://uk.rs-online.com/web/p/ac-dc-adapters/1391777/) £11.89
- [ ] [RS PRO 1.75mm White PLA 3D Printer Filament, 1kg RS Stock No. 832-0223](https://uk.rs-online.com/web/p/3d-printing-materials/8320223/) £29.17
- [ ] [Seeed Studio, SPDT Relay - 103020133. RS Stock No. 184-5099](https://uk.rs-online.com/web/p/power-motor-robotics-development-tools/1845099) £9.06
- [ ] [brennenstuhl 3m 6 Socket Type G - British Extension Lead, 230 V RS Stock No. 768-5320 ](https://uk.rs-online.com/web/p/extension-leads-cable-reels/7685320/) £19.55

## 3. To Buy

- [ ] RPi stuff (See below)
- [ ] Humidifier 
- [ ] 12V DC
- [ ] RPi Camera?
- [ ] Cooler?
---
- [ ] [JKL Components White LED Strip 5m 12V dc, ZFS-155000-CW RS Stock No. 123-1037](https://uk.rs-online.com/web/p/led-strip-lights/1231037/) £132.24, 6500ºK, 6925 lum, 159.28 umol/s PPFD
- [ ] [NEOPIXELS light?](https://www.adafruit.com/category/168)
- [ ] ? For cooling: [Semiconductor refrigerator](https://www.banggood.com/Geekcreit-12V-6A-DIY-Electronic-Semiconductor-Refrigerator-Radiator-Cooling-Equipment-p-1074404.html?akmClientCountry=CN&cur_warehouse=CN)-Banggod. Or use a liquid heat exchanger (Available on RS) but this is very very expensive (>£200)
- [ ] [grove Digital Light Sensor](https://wiki.seeedstudio.com/Sensor_light/)
- [ ] [TS 600W LED Grow Light Full Spectrum](https://marshydroled.co.uk/products/ts-600w-led-grow-light-full-spectrum-hydroponics-indoor-lamp-for-veg-flower-all-stages-plants?currency=GBP&variant=32272546332706&utm_medium=cpc&utm_source=google&utm_campaign=Google%20Shopping&gclid=Cj0KCQjwvYSEBhDjARIsAJMn0lhA42Kst5ttuClaumEVEg_mW8RPD_sweJvaoMr-Z7vDvsw-rR_fL4QaAsjIEALw_wcB)
- [ ] :star:[Intelligent LED Solutions 12-Channel Light Controller RS Stock No. 175-7451](https://uk.rs-online.com/web/p/led-lighting-controllers/1757451/?relevancy-data=7365617263685F636173636164655F6F726465723D31267365617263685F696E746572666163655F6E616D653D4931384E53656172636847656E65726963267365617263685F6C616E67756167655F757365643D656E267365617263685F6D617463685F6D6F64653D6D61746368616C6C7061727469616C267365617263685F7061747465726E5F6D6174636865643D5E5B5C707B4C7D5C707B4E647D2D2C2F255C2E5D2B24267365617263685F7061747465726E5F6F726465723D313333267365617263685F73745F6E6F726D616C697365643D59267365617263685F726573706F6E73655F616374696F6E3D267365617263685F747970653D4B4559574F52445F53494E474C455F414C5048415F4E554D45524943267365617263685F7370656C6C5F636F72726563745F6170706C6965643D59267365617263685F77696C645F63617264696E675F6D6F64653D4E4F4E45267365617263685F6B6579776F72643D494C412D31324348414E4E454C2D4C45442D54554E45522D3030312E267365617263685F6B6579776F72645F6170703D494C412D31324348414E4E454C2D4C45442D54554E45522D3030312E267365617263685F636F6E6669673D3026&searchHistory=%7B%22enabled%22%3Atrue%7D)
- [ ] https://www.adafruit.com/product/1455
- [ ] Light meter

缺货:
- [ ] [Raspberry Pi, LCD Touch Screen with 7in Capacitive Touch Screen RS Stock No. 899-7466](https://uk.rs-online.com/web/p/products/8997466/) £57.96
- [ ] [Okdo ABS Case for use with Raspberry Pi 4 in Black RS Stock No. 193-5380 ](https://uk.rs-online.com/web/p/raspberry-pi-cases/1935380/) £17.99
- [ ] [Raspberry Pi 3 B+ RS Stock No. 137-3331](https://uk.rs-online.com/web/p/products/1373331/) £33.37
- [ ] [Raspberry Pi 4 B 4GB RS Stock No. 182-2096](https://uk.rs-online.com/web/p/raspberry-pi/1822096/) £53.22

Wanted to buy but give up:
- [x] Long Rpi ribbon cable (Other suppliers?). -> Not found on RS
- [x] A better Tm and Hum sensor for calibration? -> Borrow from xxx
- [ ] camera multiplexer raspberry pi -> Not found on RS
- [ ] Wifi? -> Use Rpi
- [x] More water pump
- [x] Cutting pad (绿色)
- [x] Insulation panels (if using polystyrene box then may skip that)
- [x] 亚克力板
- [x] 电钻

## Light

1. Buy a bunch of these [LED light engines](https://i-led.co.uk/LED-Light-Engines/Ledil-Lens-Selectors/Ledil-lens-selector-OSCONIQ-P7070.php)  and use Intelligent LED Solutions 12-Channel Light Controller to control them.
2. ILS ILK-PETUNIA-01 LED Light Kit + controller
3. [Strips](https://uk.rs-online.com/web/p/led-circular-arrays/1947653/) or [Circular Array](https://uk.rs-online.com/web/p/led-circular-arrays/1946443/) at different wavelengths + controller 
4. [Horti Florence Light Wide Flowering](https://uk.rs-online.com/web/p/led-grow-lights/1874967/) 300 pounds

## Supplier 

RS Components
Farnell
CPC OneCall
Acoustic Metrology 
Advanced Wave Sensors SL
Alpha Omega
Arrow Electronics (UK) 
Ashlea Components
Aspen Electronics
Atlantic Microwave 
Audon Electronics 
Automotion Components 
Bangjiang Technology Electronic Co.
Barric 
Castle Microwave  
Chester (UK) LTD T/A Chester Machine Tools
Chromatechnic 
Coilcraft Europe 
CTS-direct.net
Dau Components  
Digi-Key Corporation
Distrelec BV
DL Instruments
Drivetek AG
EFS Manufacturing
ESR Electronic Components
Hitech Global LLC
Holroyd Components
Homechip
Impact Test Equipment
Instrotech
ITS Testing Services T/A Isodaq Technology
Microelectrodes INC
Micron Consumer Products GRoup
Mini-Circuits Europe
Mouser Electronics INC
National Institute of Standards and Technology
Newbury Electronics
Nikon Metrology Europe
NResearch UK
OCCO Coolers
Ooznest 
Pacer Components
Plasma Quest
Powersolve Electronics
Printech Circuit Laboratories
Process Parameters
Protonics
Rak Printed Circuit Boards
Reichelt Electronik
Relchron LTD T/A Protopic
RF Com 
Segen 
Semikron
Shearline Precision Engineering
Sil'tronic Silicon Technologies
Siltronic SAS
Sparkfun Electronics
Sterling Sensors
Survey Supplies T/A Korec
Techni Measure
Technical Manufacturing Corporation
Tectra GMBH
Tektronic UK
Toolworld
Unmanned Tech
Ushio UK  
Wuhan Land Electronics Co

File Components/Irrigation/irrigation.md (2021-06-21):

## Equipment

A [mini water pump](https://www.ebay.co.uk/itm/122508463023) powered by 5V on the Arduino board

## Duration

As tested on 16.6.2021, it requires about 300-400ml water to fully irrigate completely dry soil on the 24-well-plate_2.0. Water pump should first turn on for 6 sec, then shut for 10 min to dampen the soil, then turn on again for 6 sec to fully wet the soil.

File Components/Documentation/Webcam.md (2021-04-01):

# Real-time monitoring using Raspberry pi

This is file shows how to set up a webcam with Raspberry pi and upload images to Adafruit-IO for real-time monitoring.

## Device

Pi, webcam (connect with USB), PC (I am using a Linux)

## Hardware setup

<mark> Add how to setup Rpi and assembly Rpi camera module here (if necessary).

## Software setup

Video streaming using Adafruit.io. Most information is found in this [article](xxx). Read more about Adafruit Dashboard [here](https://learn.adafruit.com/adafruit-io-basics-dashboards).

### I. Adafruit IO

1. Sign up an account on [Adafruit.io](https://io.adafruit.com/).
2. You might have been redirected to accounts.adafruit.com, now go back to io.adafruit.com/ and login.
3. Go to 'Dashboard' > 'view all'.
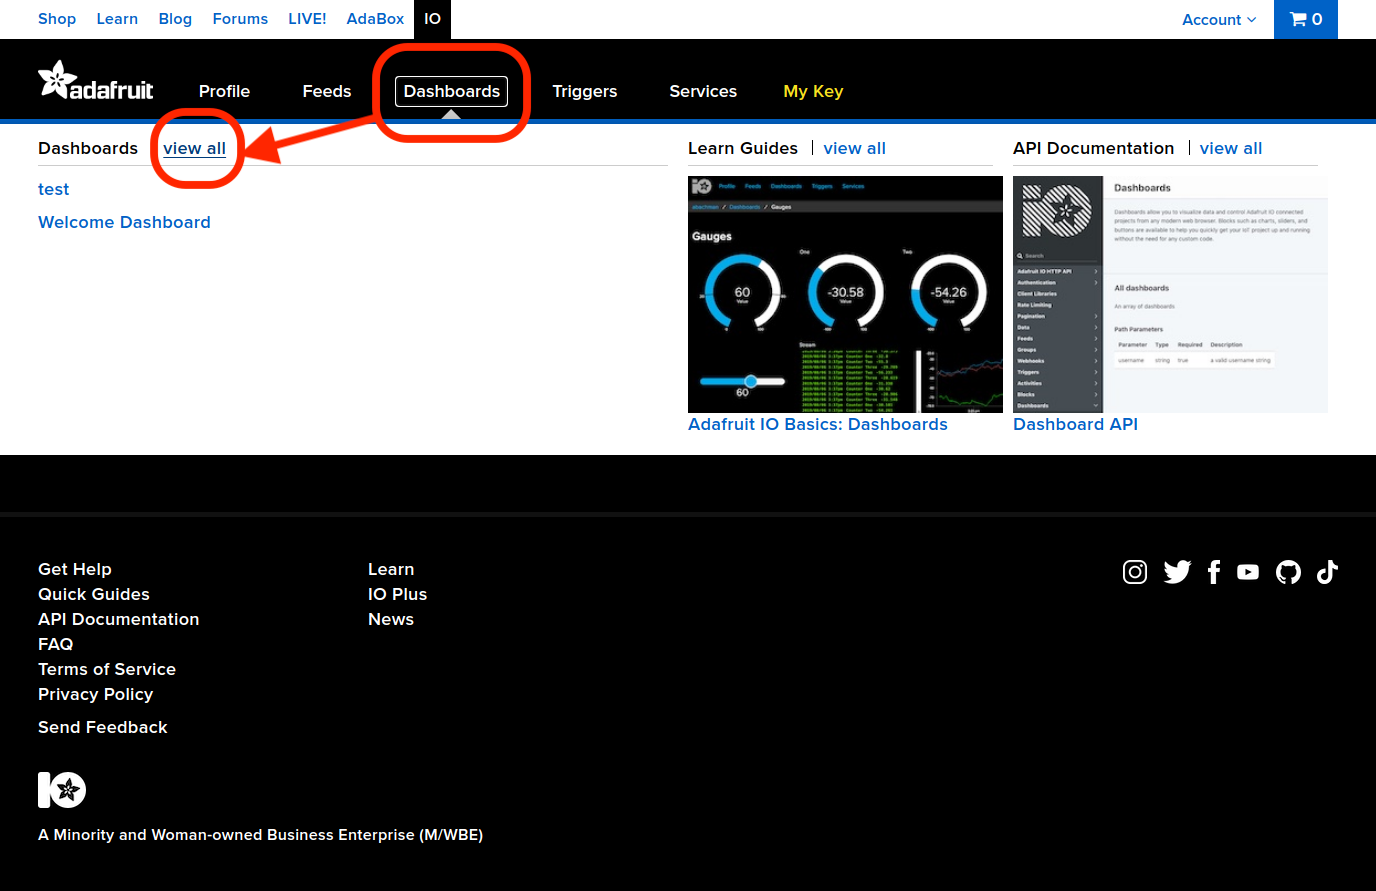
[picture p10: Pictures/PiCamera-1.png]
PiCamera Instruction
   
   Then click '+New Dashboard', enter a name and click on it.
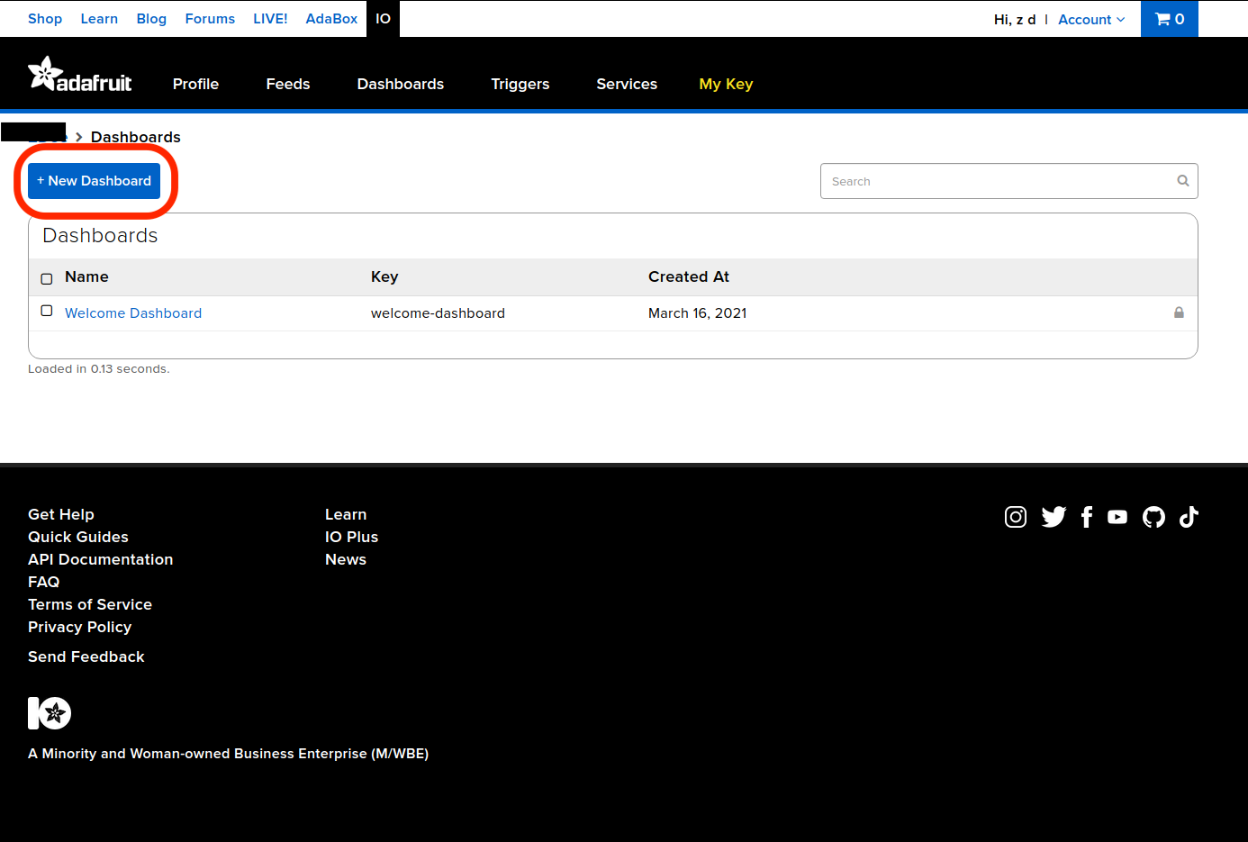
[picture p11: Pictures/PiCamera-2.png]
PiCamera Instruction
   
4. Click the gear button and select 'create new block'.
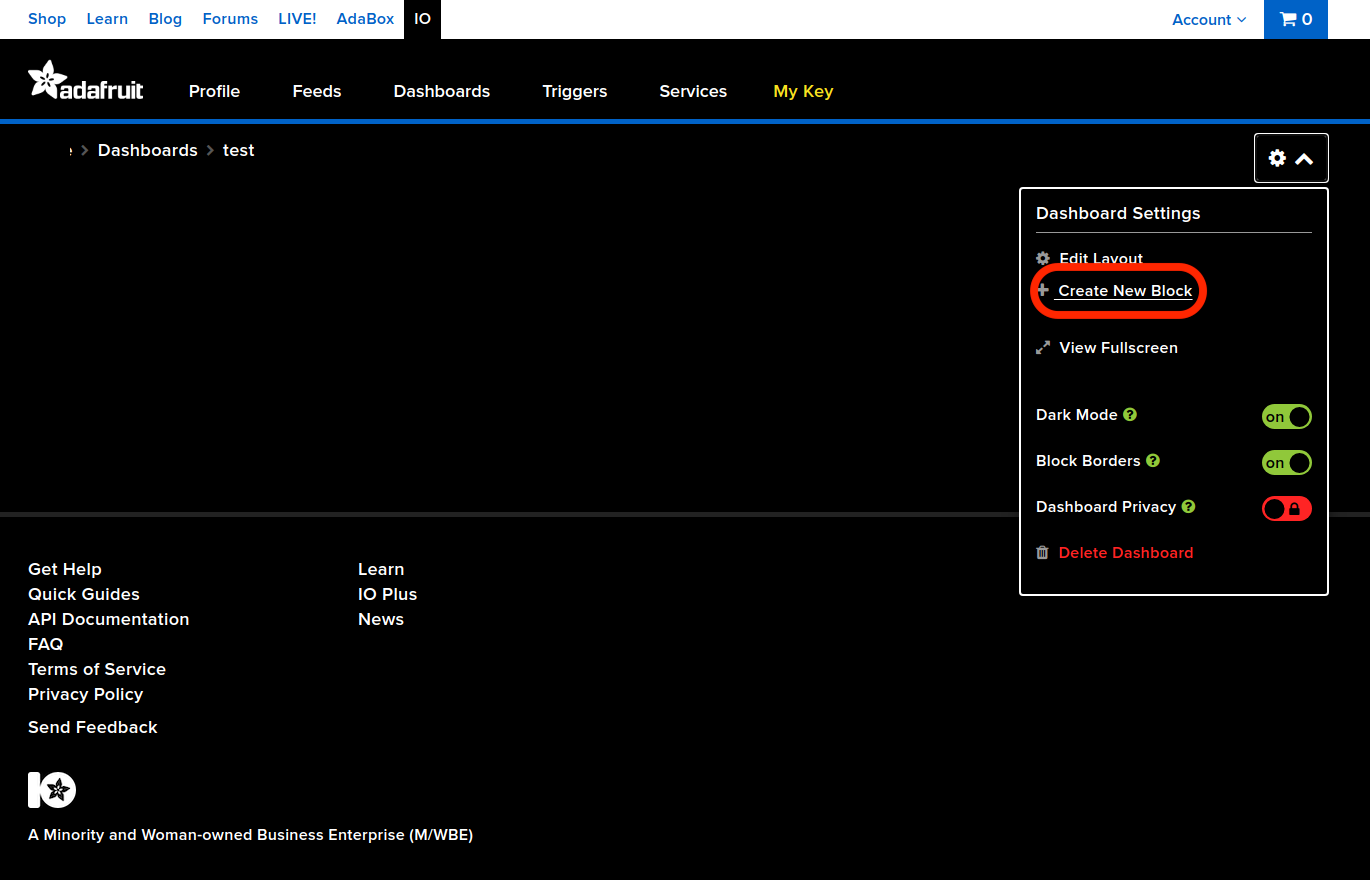
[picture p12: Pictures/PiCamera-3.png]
PiCamera Instruction
   
   We need the image block for video steaming.
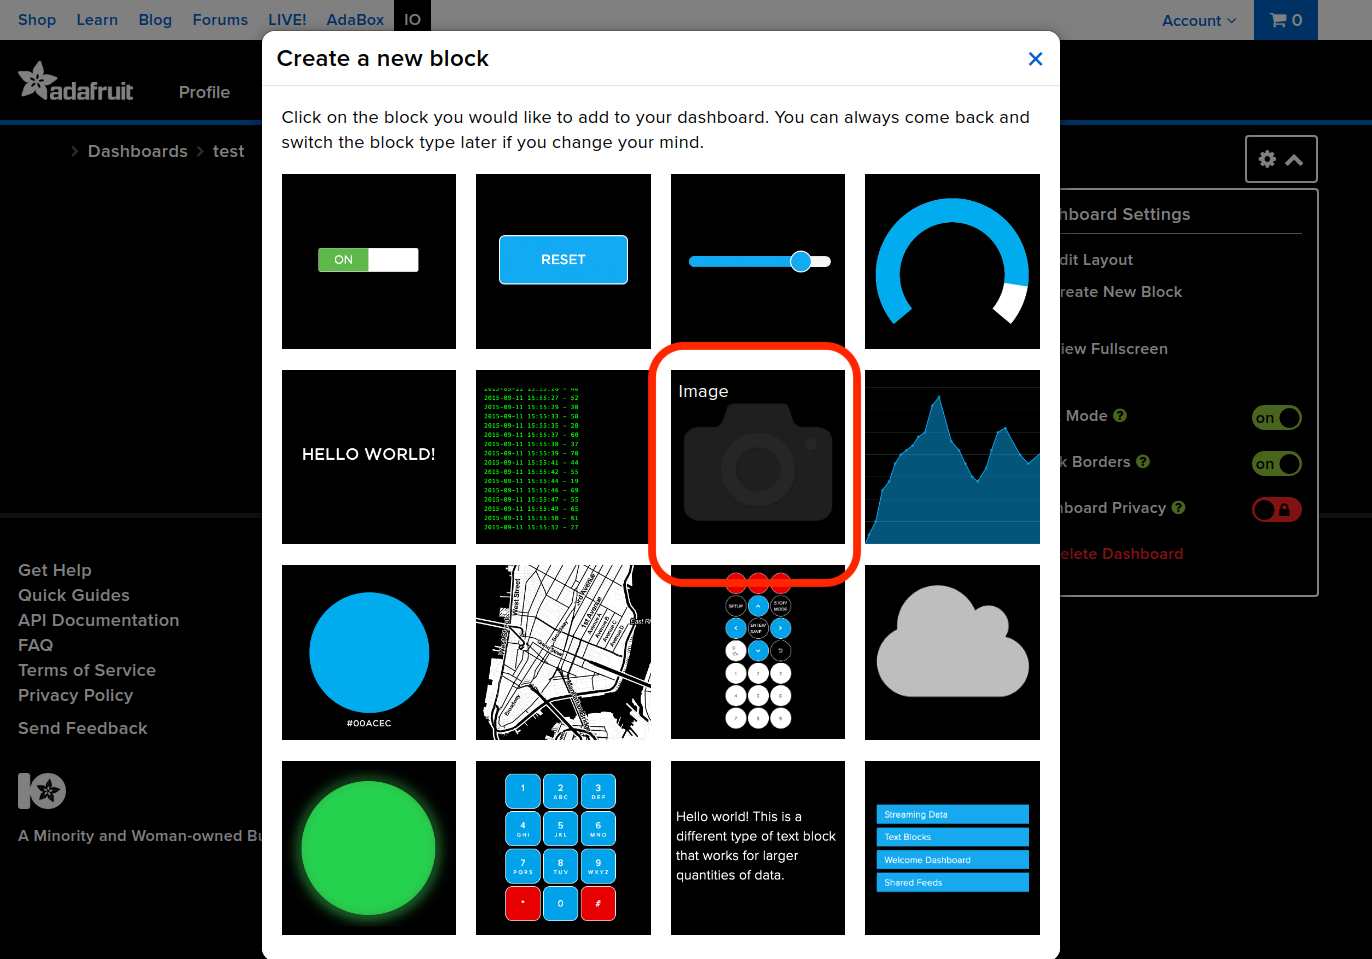
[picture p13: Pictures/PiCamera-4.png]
PiCamera Instruction
   
5. Enter a name for the feed. Select it and go to 'Next step'. On the next page you could put some more details to describe this block. When finished, click 'Create block'.
   >Feed is where data from each sensor is stored, in our case this is where the video from Raspberry Pi camera will be pushed to.
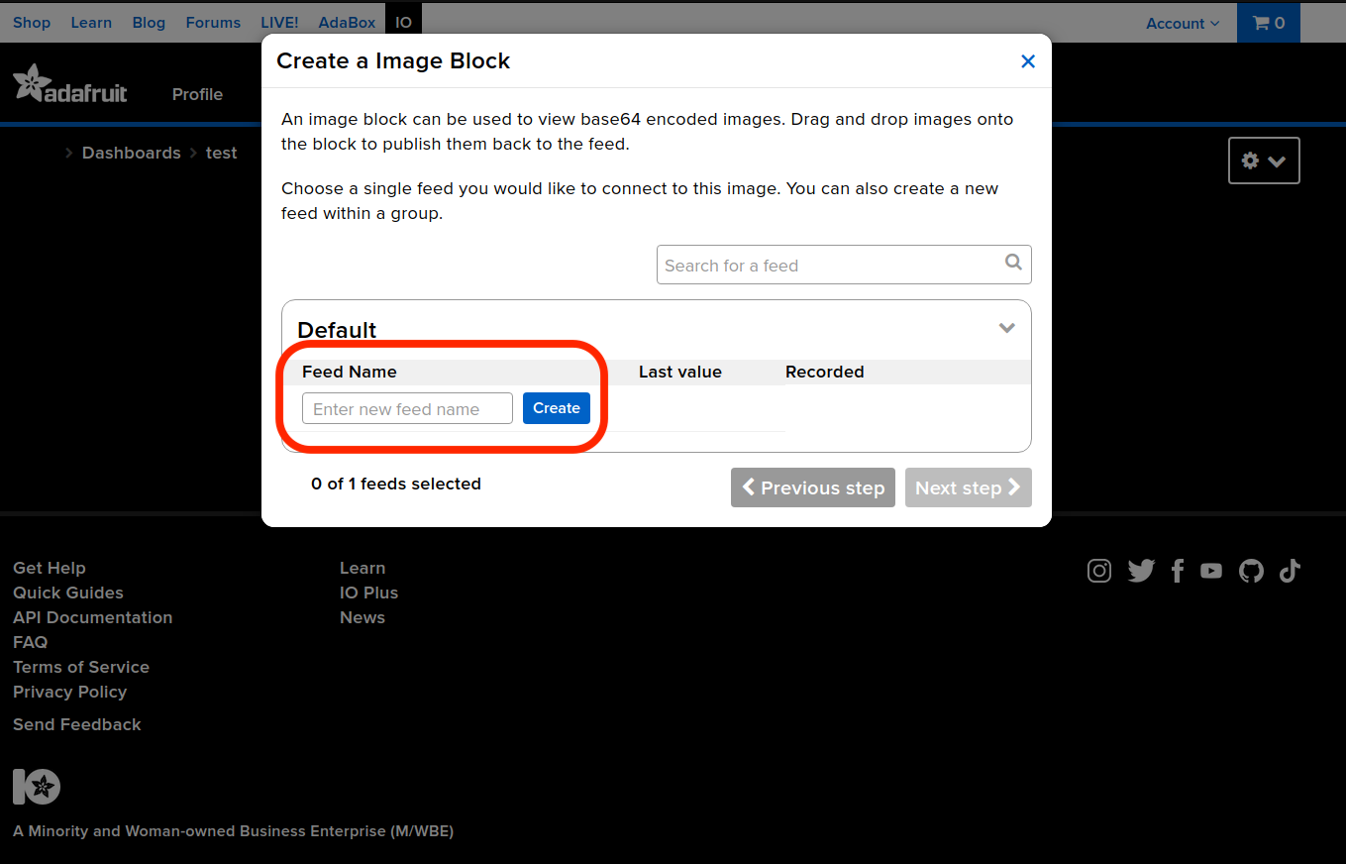
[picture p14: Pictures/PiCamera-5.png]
PiCamera Instruction
   
6. Now you can go to 'Feeds' to see the feed you just created. This is where you can view your data and change settings.
7. In order to setup software on Raspberry Pi in the next section, go to 'My Key' and you could find the 'Username' and 'Active Key' that you will need later.

### II. Raspberry Pi Setup

1. Install [`fswebcam`](https://www.raspberrypi.org/documentation/usage/webcams/) package on Raspberry Pi:

```bash
sudo apt install fswebcam
```

`fswebcam` is an easy command line package to take pictures using your webcam. The command that we are going to use in our python script is:

```bash
fswebcam -q -r 1280x720 --no-banner --jpeg 60 --save /home/pi/Camera/snapshot.jpg'
```

The `-q` flag makes `fswebcam` to work in quite mode and hides all output messages except for errors. `-r` flag specifies the resolution of the image that we are going to take, here I use 1280*720 as this is the highest resolution supported by my camera. `--no-banner` tells `fswebcam` not to include any text information in the image. `--jpeg 60` specifies the quality of the jpeg images, which is limited by the size of individual data that can be uploaded to Adafruit-IO at each time (100kb). `--save` defines the location and name of snapshot images taken by `fswebcam`. The python script will also be put in that location. These parameters can be adjusted accordingly.

2. Run the [python script](webcam-fswebcam.py) that takes an image every 2 seconds and upload it to Adafruit-IO. You may need to install some of the dependencies with `pip` or `pip3`.

## Archived-Motion method

### Motion configuration

```json
width 1024
height 768
output_pictures off
snapshot_interval 2
snapshot_filename snap
on_picture_save python3 /home/pi/Camera/webcam.py
```

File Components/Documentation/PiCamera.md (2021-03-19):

# Real-time monitoring using Raspberry pi

This is a file showing how to set up Raspberry pi camera for real-time monitoring.

## Device

Pi, camera, PC (I am using a Linux)

## Hardware setup

<mark> Add how to setup Rpi and assembly Rpi camera module here (if necessary).

## Software setup

Video streaming using Adafruit.io. Most information is found in this [article](https://iotdesignpro.com/projects/iot-raspberry-pi-cloud-camera-stream-video-from-raspberry-pi-to-cloud), but some details are out of date and some changes were made accordingly. Also refer to this [article](https://learn.adafruit.com/cloud-cam-connected-raspberry-pi-security-camera/adafruit-io). Read more about Adafruit Dashboard [here](https://learn.adafruit.com/adafruit-io-basics-dashboards).

### I. Adafruit IO

1. Sign up an account on [Adafruit.io](https://io.adafruit.com/).
2. You might have been redirected to accounts.adafruit.com, now go back to io.adafruit.com/ and login.
3. Go to 'Dashboard' > 'view all'.
   PiCamera Instruction
   Then click '+New Dashboard', enter a name and click on it.
   PiCamera Instruction
4. Click the gear button and select 'create new block'.
   PiCamera Instruction
   We need the image block for video steaming.
   PiCamera Instruction
5. Enter a name for the feed. Select it and go to 'Next step'. On the next page you could put some more details to describe this block. When finished, click 'Create block'.
   >Feed is where data from each sensor is stored, in our case this is where the video from Raspberry Pi camera will be pushed to.
   PiCamera Instruction
6. Now you can go to 'Feeds' to see the feed you just created. This is where you can view your data and change settings.
7. In order to setup software on Raspberry Pi in the next section, go to 'My Key' and you could find the 'Username' and 'Active Key' that you will need later.

### II. Raspberry Pi Setup

1. Install Node.js on Raspberry Pi.

```bash
curl -sL https://deb.nodesource.com/setup_10.x | sudo bash 
sudo apt install nodejs
```

2. Check if Node.js is installed successfully by checking their versions:

```bash
node –v
npm –v
```

On my computer they were:

```bash
v10.24.0
6.14.11
```

3. Install ‘adafruit-io-camera’ on Raspberry Pi to monitor Pi camera and send pictures to an Adafruit IO feed. This may take some time.

```bash
sudo apt-get update
sudo apt-get install -y imagemagick
sudo npm install --global --no-optional forever forever-service adafruit-io-camera
```

1. After adafruit-io-camera is installed, use your ‘Username’ and ‘AIO Key’ to configure your Adafruit IO account on Raspberry Pi. Replace your username and AIO key on the place of ‘YOUR-USERNAME’ and ‘AIO-KEY’ respectively, which can be found under 'My Key' on io.adafruit.

```bash
adafruit-io camera config --username YOUR-USERNAME --key AIO-KEY
```

5. Now start your camera using the following command, replace ‘pi-camera’ with the name of feed that you just created.

```bash
adafruit-io camera start -f pi-camera -r 2
```

 The '-r' flag specifies timelapse capture rates in seconds, i.e. it is writing a new image to the feed every 2 seconds here. This is limited by the 30 data points per minute provided by the free IO account. If you upgrade your IO account then it will be able to accept 60 data points per minute, therefore you would be able to change -r to 1.

When not in use you can stop pushing video to Adafruit IO by:

```bash
adafruit-io camera stop
```

Next time when you want to start camera again, simply do

```bash
adafruit-io camera start
```

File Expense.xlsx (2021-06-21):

Item | Price | Number | Total price | Total price | Company | Stock Number | Link | Date | Document on Hackster?
Raspberry Pi 4 B 4GB | 53.22 | 2 | 106.44 | 273.37 | RS | 182-2096 |  | 2020-12-21 | Y
Two Sandisk Storage Card 16Gb | 9.204 | 2 | 18.408 |  | RS | 121-3897 |  | 2020-12-21 | N
Okdo Raspberry Pi Power Supply, USB Type C with Universal Plug Type, 1.5m | 7.62 | 2 | 15.24 |  | RS | 187-1381 |  | 2020-12-21 | N
LCD Touch Screen with 7in Capacitive Touch Screen | 57.96 | 1 | 57.96 |  | RS | 899-7466 |  | 2020-12-21 | Y
DesignSpark ABS Case | 17.99 | 1 | 17.99 |  | RS | 117-6025 |  | 2020-12-21 | N
SAD-01, Breadboard Prototyping Board | 17.988 | 1 | 17.988 |  | RS | 453-8824 | https://uk.rs-online.com/web/p/breadboards/4538824/ | 2020-12-21 | Y
1.75mm Black PLA 3D Printer Filament, 300g | 12.288 | 1 | 12.288 |  | RS | 832-0406 | https://uk.rs-online.com/web/p/3d-printing-materials/8320406/ | 2020-12-21 | N
Raspberry Pi, Camera | 24.12 | 1 | 24.12 |  | RS | 913-2664 | https://uk.rs-online.com/web/p/raspberry-pi-cameras/9132664/ | 2020-12-21 | Y
heating element | 17.304 | 2 | 34.608 | 165 | RS | 299-5950 |  | 2021-02-01
Bostik Bond-Flex 100HMA Black Sealant Non-Slump Paste 300 ml Cartridge | 7.596 | 1 | 7.596 |  | RS | 341-0955 |  | 2021-02-01
Seeed Studio 101020513, Grove-Temperature, Humidity, Pressure and Gas Sensor (BME680) for BME680 | 18.756 | 3 | 56.268 |  | RS | 184-5086 |  | 2021-02-01 | Y
Raspberry Pi 1m HDMI to Micro HDMI Cable in Black. | 4.728 | 2 | 9.456 |  | RS | 187-1377 |  | 2021-02-01
Laserliner 082.034A Digital Hygrometer | 28.8 | 1 | 28.8 |  | RS | 191-9564 |  | 2021-02-01
Okdo ABS Case in Black. | 4.68 | 1 | 4.68 |  | RS | 187-3799 |  | 2021-02-01
RS PRO 1kΩ Carbon Film Resistor 2W ±5%. | 0.996 | 1 (pack of 10) | 0.996 |  | RS | 707-8861 |  | 2021-02-01
RS PRO 10kΩ Carbon Film Resistor 2W ±5% | 0.996 | 1 (pack of 10) | 0.996 |  | RS | 707-8906 |  | 2021-02-01
12 V dc, DC Axial Fan, 60 x 60 x 25mm, 39.1m³/h, 2.8W. | 7.86 | 1 | 7.86 |  | RS | 668-8827 |  | 2021-02-01
Sandisk Storage Card for Raspberry Pi, 16GB NOOBs | 9.2 | 3 | 27.6 | 27.6 | RS | 121-3897 | https://uk.rs-online.com/web/p/raspberry-pi-os/1213897/ | 2021-02-25 | N | Previous cards were damaged
RS PRO 0.8MP 30fps Webcam, 1080 x 720 | 66 | 1 | 66 | 114.57 | RS | 201-3517 | https://uk.rs-online.com/web/p/products/2013517/ | 2021-03-18 | N
Seeed Studio, Grove Base Shield V2 | 6.7 | 1 | 6.7 |  | RS | 174-3233 | https://uk.rs-online.com/web/p/products/174-3233/ | 2021-03-18 | N
Seeed Studio 110990210 for use with Grove-Base Shield | 2.54 | 5 | 12.7 |  | RS | 179-3726 | https://uk.rs-online.com/web/p/products/179-3726/ | 2021-03-18 | N
Seeed Studio, SPDT Relay - 103020133 | 9.06 | 1 | 9.06 |  | RS | 184-5099 | https://uk.rs-online.com/web/p/power-motor-robotics-development-tools/1845099 | 2021-03-18 | N
N-Channel MOSFET, 33 A, 100 V, 3-Pin TO-220AB Infineon IRF540NPBF, pack of 20 | 12.28 | 1 | 12.28 |  | RS | 914-8154 | https://uk.rs-online.com/web/p/mosfets/9148154/ | 2021-03-18 | N
Clever Little Box, CLB Cable Mount DC Jack Socket, 1Pole 1A | 2.78 | 1 | 2.78 |  | RS | 810-4605 | https://uk.rs-online.com/web/p/jack-plugs-sockets/8104605/ | 2021-03-18 | N
XP Power,12V dc, 5W Plug In Power Supply, 420mA, Level VI Efficiency, 1 Output Switched Mode Power Supply, Type G | 1 | 1 | 1 |  | RS | 121-7133 | https://uk.rs-online.com/web/p/ac-dc-adapters/1217133/ | 2021-03-18 | N
RS PRO Black Cable Tie Nylon, 300mm x 4.8 mm, pack of 100 | 13.25 | 1 | 13.25 |  | RS | 233-487 | https://uk.rs-online.com/web/p/products/0233487/ | 2021-03-18 | N
ON Semiconductor ALS-GEVB, Ambient Light Sensor (ALS) Shield Evaluation Board Evaluation Board for NOA1305CUTAG | 6.26 | 1 | 6.26 | 224.63 | RS | 171-9122 | https://uk.rs-online.com/web/p/sensor-development-tools/1719122/
brennenstuhl 3m 6 Socket Type G - British Extension Lead, 230 V | 19.55 | 1 | 19.55 |  | RS | 768-5320 | https://uk.rs-online.com/web/p/extension-leads-cable-reels/7685320/
RS PRO 1.75mm White PLA 3D Printer Filament, 1kg | 29.17 | 1 | 29.17 |  | RS | 832-0223 | https://uk.rs-online.com/web/p/3d-printing-materials/8320223/
RS PRO Silicone Heater Mat, 5 W, 50 x 100mm, 12 V dc | 22.21 | 1 | 22.21 |  | RS | 245-528 | https://uk.rs-online.com/web/p/heater-pads/0245528/
ILS ILK-PETUNIA-01 LED Light Kit, OSLON SSL Petunia | 145.6 | 1 | 145.6 |  | RS | 875-0037 | https://uk.rs-online.com/web/p/led-kits/8750037/
RS PRO UK Mains Connector BS 1363, 13A, Cable Mount, 250 V ac | 6.1 | 1 | 6.1 |  | RS | 854-380 | https://uk.rs-online.com/web/p/mains-plugs-sockets/0854380/
TE Connectivity 1776293-2 Terminal Strip, 30A, 250 V Screw Screw | 1.68 | 10 | 16.8 |  | RS | 782-2857 | https://uk.rs-online.com/web/p/standard-terminal-blocks/7822857?matchtype=&aud-826607888547:pla-302090786601&gclsrc=aw.ds
HellermannTyton Adhesive Lined Heat Shrink Tubing, Black 4mm Sleeve Dia. x 1.2m Length 4:1 Ratio, TA42 Series | 4.45 | 1 | 4.45 |  | RS | 914-6802 | https://uk.rs-online.com/web/p/heat-shrink-cold-shrink-sleeves/9146802/
Sandisk Micro SD Card 128 GB MicroSDXC Card Class 10, UHS-1 U1 | 69.34 | 1 | 69.34 | 217.836 | RS | 174-7340 | https://uk.rs-online.com/web/p/micro-sd-cards/1747340
RS PRO RS41 K Input Wired Digital Thermometer | 47.18 | 1 | 47.18 |  | RS | 123-1940 | https://uk.rs-online.com/web/p/products/1231940/
RS PRO Digital Timer Switch 230 V ac 100h | 18.56 | 1 | 18.56 |  | RS | 178-5368 | https://uk.rs-online.com/web/p/time-switches/1785368/
RS PRO, 24 V dc, DC Axial Fan, 80 x 80 x 25mm, 68m³/h, 2.4W | 9.72 | 1 | 9.72 |  | RS | 668-8833 | https://uk.rs-online.com/web/p/axial-fans/6688833/
Fan Filter, Fan Mounted 86.5 x 86.5mm, for 80mm Fan PET | 5.82 | 1 | 5.82 |  | RS | 221-336 | https://uk.rs-online.com/web/p/fan-filters/0221336/
RS PRO, 20W Plug In Power Supply 24V ac, 800mA Type G | 11.89 | 1 | 11.89 |  | RS | 139-1777 | https://uk.rs-online.com/web/p/ac-dc-adapters/1391777/
RS PRO 1.75mm White PLA 3D Printer Filament, 1kg | 29.17 | 1 | 29.17 |  | RS | 832-0223 | https://uk.rs-online.com/web/p/3d-printing-materials/8320223/
Seeed Studio, SPDT Relay – 103020133 | 9.06 | 1 | 9.06 |  | RS | 184-5099 | https://uk.rs-online.com/web/p/power-motor-robotics-development-tools/1845099
brennenstuhl 3m 6 Socket Type G - British Extension Lead, 230 V | 19.55 | 1 | 19.55 |  | RS | 768-5320 | https://uk.rs-online.com/web/p/extension-leads-cable-reels/7685320/
Remain |  |  |  | 1976.994

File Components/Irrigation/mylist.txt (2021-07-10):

file '20210616.mp4'
file '20210616_2.mp4'
file '20210616_3.mp4'
file '20210616_4.mp4'

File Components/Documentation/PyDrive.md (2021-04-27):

# PyDrive

This documents how to set up PyDrive on Rpi to upload figures and csv files to google drive.

Refer to official documentation [here](https://googleworkspace.github.io/PyDrive/docs/build/html/index.html).

## Install PyDrive

```bash
pip3 install PyDrive
```

## PyDrive configuration

Official document is [here](https://googleworkspace.github.io/PyDrive/docs/build/html/quickstart.html#authentication) but it didn't work for me. I did some minor modifications:

1. Go to APIs Console and make your own project.
2. Search for ‘Google Drive API’, select the entry, and click ‘Enable’.
3. Select ‘Credentials’ from the left menu, click ‘Create Credentials’, select ‘OAuth client ID’.
4. Now, the product name and consent screen need to be set -> click ‘Configure consent screen’ and follow the instructions. Once finished: Select ‘Application type’ to be Desktop application.
5. Enter an appropriate name.
6. Click ‘Create’.
7. Click ‘Download JSON’ on the right side of Client ID to download client_secret_<really long ID>.json.
8. The downloaded file has all authentication information of your application. Rename the file to “client_secrets.json” and place it in your working directory.
9. Create a quickstart.py file and copy and paste the following code.

```python
from pydrive.auth import GoogleAuth

gauth = GoogleAuth()
gauth.CommandLineAuth()
```

Run quickstart.py and follow the authorizations from command lines as a quick test that connection is working.

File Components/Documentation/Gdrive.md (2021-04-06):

# Google drive

>This document is not longer used, as I only want to upload single file to google drive at a time instead of sync a whole folder. Use the python package [PyDrive](https://googleworkspace.github.io/PyDrive/docs/build/html/index.html) instead, check [this](PyDrive.md).

This documents how to set up google drive sync on Rpi to save a copy of data and images on cloud.

Ref: We use [Grive2](https://github.com/vitalif/grive2) here. Alternative: [drive](https://github.com/odeke-em/drive) and [rclone](https://medium.com/@artur.klauser/mounting-google-drive-on-raspberry-pi-f5002c7095c2).

## Installing Grive2

Refer to official documentation [here](http://yourcmc.ru/wiki/Grive2#Installation).

Install all dependencies by

```bash
sudo apt-get update
sudo apt-get install git cmake build-essential libgcrypt20-dev libyajl-dev libboost-all-dev libcurl4-openssl-dev libexpat1-dev libcppunit-dev binutils-dev debhelper zlib1g-dev dpkg-dev pkg-config
```

Then clone the repo (or just [download the zip file](https://github.com/vitalif/grive2/archive/master.zip) and unzip it) and cd into it.

```bash
git clone https://github.com/vitalif/grive2
cd grive2
```

Install by

```bash
mkdir build
cd build
cmake ..
make -j4
sudo make install
```

If installation is successful then you should be able to run `grive` from command line. By `grive -v` I got

```bash
grive version 0.5.2-dev Apr  6 2021 11:15:37
```

## Google Drive configuration

Google restricted access for unapproved applications so there are a few more steps required to configure Grive2. Follow instructions [here](https://github.com/Dishendramishra/linux-setup/blob/master/README.md#google-drive).

Note: following on the steps shown above, make sure you go to OAuth 'consent screen' > 'Test Users' > 'ADD USERS' and add your email there.

## Usage

When running Grive2 for the first time, we need to run `grive -a` with OAuth2 details to grant permission to Grive to access to your Google Drive.

```bash
cd <path-to-your-directory>
grive -a --id <client_id> --secret <client_secret>
```

 Follow the steps to authenticate the OAuth2 client to allow it to access your drive folder.

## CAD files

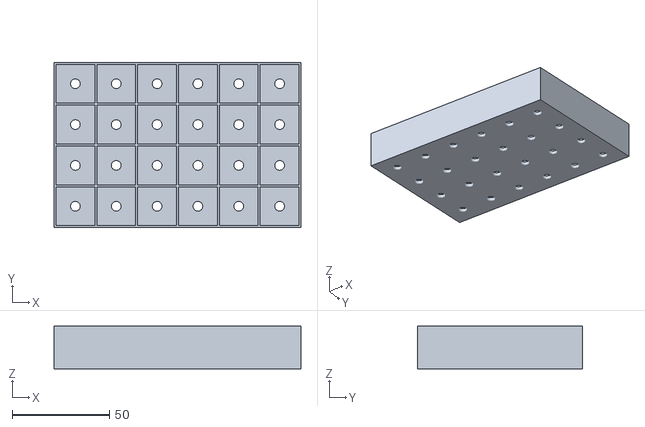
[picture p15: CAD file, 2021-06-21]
3D/Plate/24-well-plate_2.0.stl
127.0 x 85.0 x 22.0

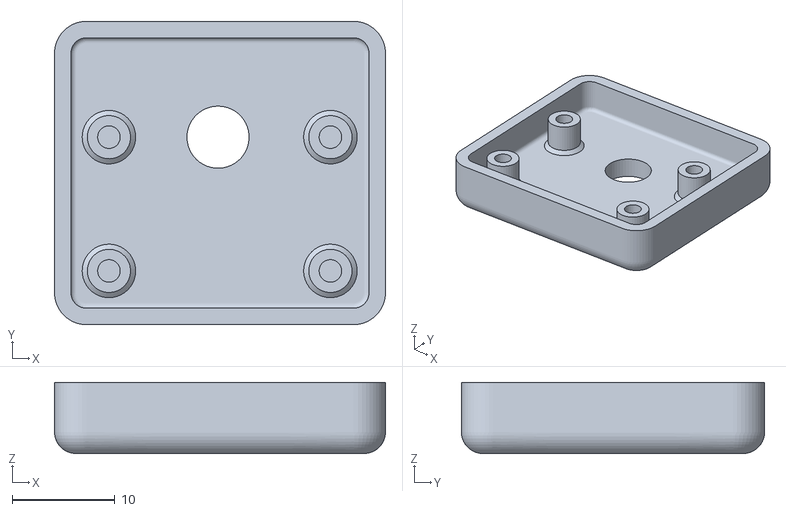
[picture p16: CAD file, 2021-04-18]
3D/Raspberry_Pi_Camera_Case_and_Tripod/Picam-front.stl
32.2 x 29.5 x 6.90

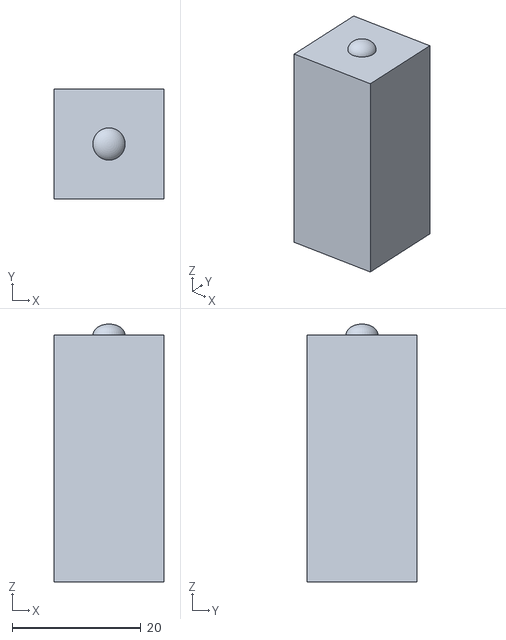
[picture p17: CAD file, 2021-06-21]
3D/Plate/Tamp_2.0.stl
17.0 x 17.0 x 40.0

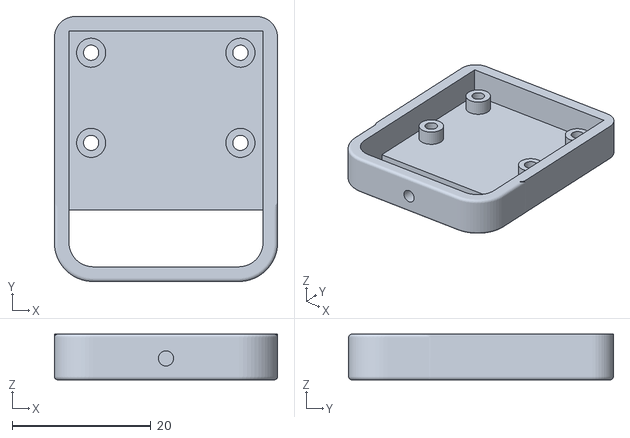
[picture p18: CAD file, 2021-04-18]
3D/Raspberry_Pi_Camera_Case_and_Tripod/picam-back.stl
32.2 x 38.2 x 6.60

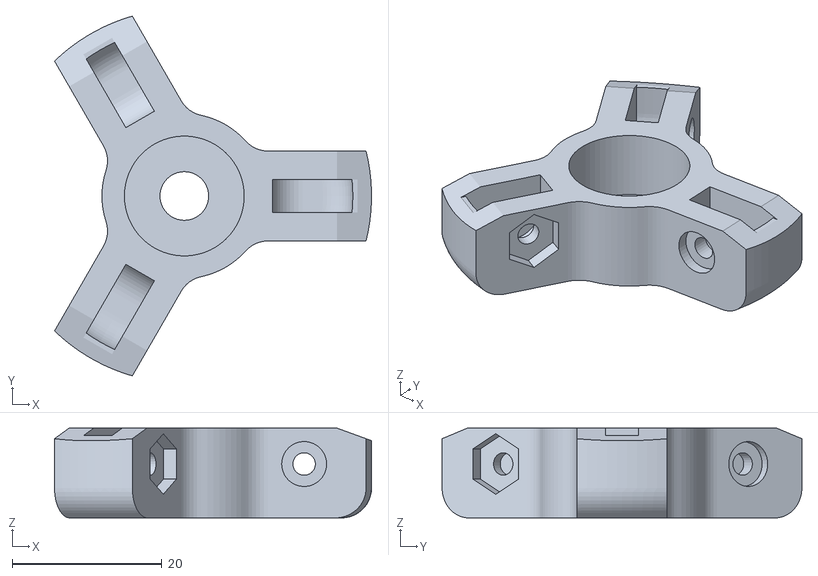
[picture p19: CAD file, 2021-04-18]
3D/Raspberry_Pi_Camera_Case_and_Tripod/tripod-base.stl
42.3 x 48.0 x 12.0

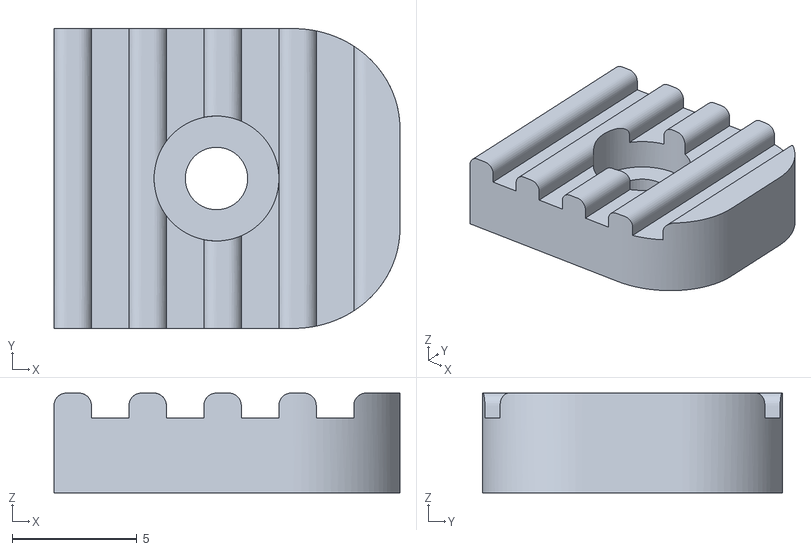
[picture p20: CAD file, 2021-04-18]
3D/Raspberry_Pi_Camera_Case_and_Tripod/tripod-foot.stl
13.9 x 12.0 x 4.00

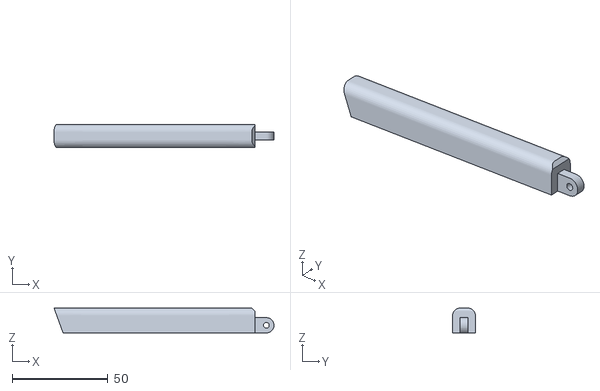
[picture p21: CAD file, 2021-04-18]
3D/Raspberry_Pi_Camera_Case_and_Tripod/tripod-leg.stl
114.7 x 12.0 x 13.0

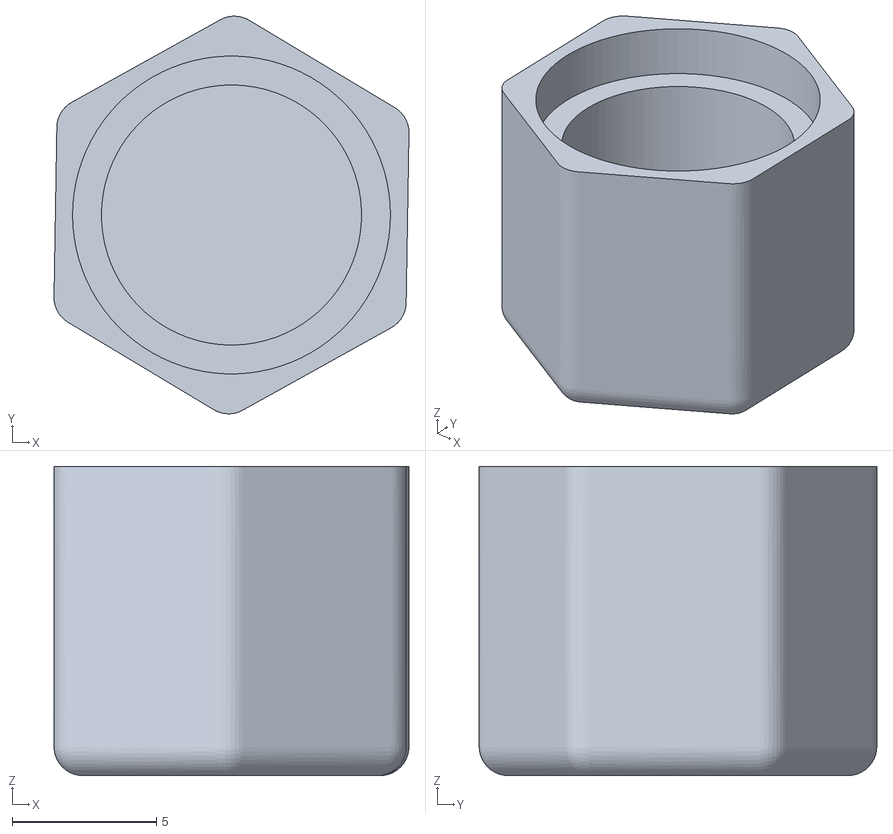
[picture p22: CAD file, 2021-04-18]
3D/Raspberry_Pi_Camera_Case_and_Tripod/picam-adapter.stl
12.3 x 13.8 x 10.7

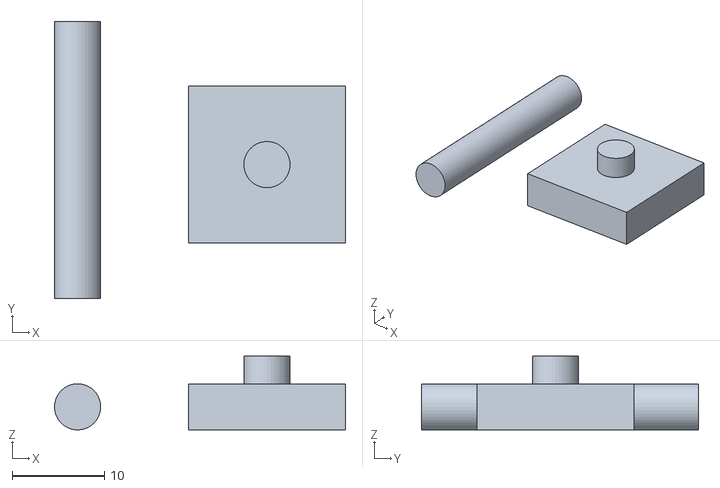
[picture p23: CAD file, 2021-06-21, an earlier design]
3D/Plate/Archive/Tamp_1.1.stl
31.5 x 30.0 x 8.00

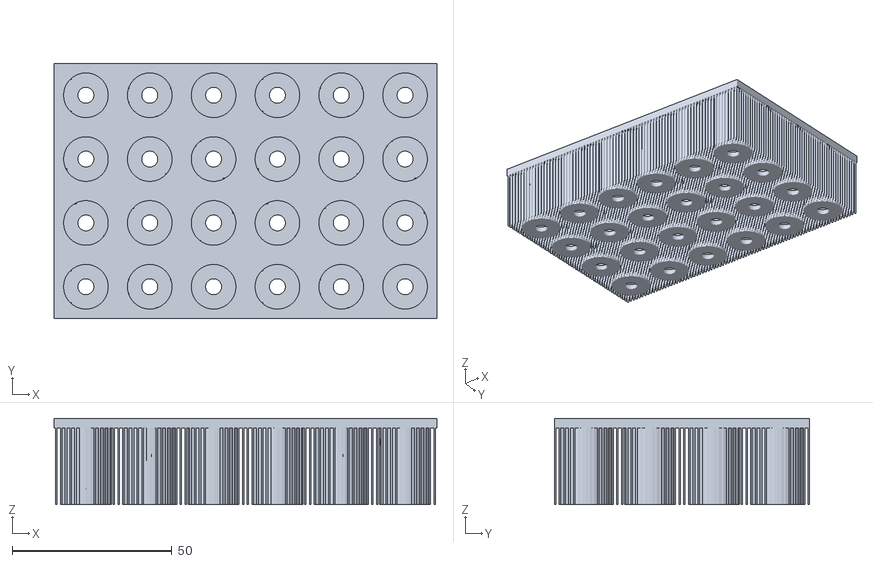
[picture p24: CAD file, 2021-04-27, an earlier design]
3D/Plate/Archive/24-well-plate_1.0.stl
120.0 x 80.0 x 27.0

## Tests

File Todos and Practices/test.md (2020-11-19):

this is a sentence on 'zd' branch that zd wrote at 11.00.

And this is added after 'zd' branch was created and the first push.

# Workflow
Git workflow https://www.atlassian.com/git/tutorials/comparing-workflows.  
Based on this, I think we can just have one branch (master) and both work on this. General workflow is to
1. make local changes, add, commit.
2. git pull --rebase origin master # this pull any new changes made on remote since last sync to local repo. The reason to 'rebase' is that I guess we have a more or less linear working process than each of us working on a specific feature (at the moment...). 
3. git push origin master # this publish local changes to remote.

Or have a short-live branch:
1. git branch -b new-short-branch
2. make local changes, add, commit.
3. git checkout master # this moves us back to master branch (which will be the receiving branch)
4. git merge new-short-branch # presume that the new branch was very short so no new change has happened on remote master branch, then we can directly run 'merge'
5. git branch -d new-short-branch # delete the short-live branch as it won't be useful.

This is a test by Weiming using GitHub Desktop on Mac.  
GitHub Desktop just provides a Graphical User Interface(GUI), but essentially all functions can be achieved through command line.

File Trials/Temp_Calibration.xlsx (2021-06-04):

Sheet: Sheet2
Date | Time(H.M.S) | Temp_LM75/oC | Temp_BME680/oC | Temp_NTC/oC | Pressure/kPa | Humidity_BME/% | Temp_RS | Temp_Laserliner | Humidity_Laserliner/%
210429 | 09.47.59 | 24.46 | 33.31 | 30.58 | 101 | 28.36 | 32 | 31.7 | 32
210429 | 10.22.02 | 24.46 | 34.06 | 31.02 | 101.01 | 28.22 | 32.1 | 32.3 | 31
210429 | 10.56.01 | 24.46 | 33.63 | 31.21 | 101.03 | 27.64 | 32.5 | 32.3 | 30
210429 | 11.30.17 | 23.96 | 33.61 | 31.12 | 101.04 | 30.31 | 31.9 | 32.1 | 32
210429 | 12.04.27 | 23.46 | 33.36 | 31.02 | 101.05 | 28.43 | 32.2 | 32 | 30
210429 | 12.38.35 | 23.46 | 33.35 | 30.93 | 101.07 | 29.04 | 31.6 | 31.8 | 30
210429 | 13.12.43 | 23.96 | 33.49 | 31.1 | 101.09 | 26.36 | 32.2 | 32.1 | 28
210429 | 13.46.52 | 24.46 | 33.63 | 31.17 | 101.11 | 28.82 | 32 | 32.1 | 30
210429 | 14.20.59 | 23.96 | 33.82 | 31.45 | 101.13 | 29.19 | 32.6 | 32.5 | 30
210429 | 14.55.05 | 23.96 | 33.25 | 31.1 | 101.12 | 30.14 | 32.1 | 32 | 31
210429 | 15.29.15 | 23.46 | 33.41 | 31.13 | 101.12 | 29.39 | 32.2 | 32 | 30
210429 | 16.03.28 | 23.46 | 32.92 | 30.82 | 101.11 | 29.6 | 31.8 | 31.7 | 30
210430 | 16.37.54 | 23.46 | 33.13 | 30.82 | 101.14 | 30.01 | 31.9 | 31.8 | 30
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

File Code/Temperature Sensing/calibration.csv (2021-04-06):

Date | Time | Standard Tm | Tm-BME | Tm-NTC | Standard Hum | Hum-BME
2021.4.6 | 10.33 | 19.4 | 20.4 | 19.5 | 77 | 78
2021.4.6 | 12.01 | 19.1 | 20.39 | 19.54 | 76 | 77.38
2021.4.6 | 13.29 | 19.7 | 20.41 | 19.52 | 81 | 77.88
2021.4.6 | 14.55 | 19.3 | 20.42 | 19.62 | 72 | 77.57
2021.4.6 | 16.20 | 19.0 | 20.44 | 19.62 | 72 | 77.6

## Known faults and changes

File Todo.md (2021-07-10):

# Todo list

## Urgent

- [ ] A new plate and a presser

## Workflow

This is to clarify priority.

Last update: 27.4.21

0. [x] [Application](#application-done) and first-month 'report'
1. [x] [Che]Sensors assembly: Seeed thermo&humidity sensor, light sensor.
2. [ ] [Che]Temperature and light control.
3. [x] [Debug]Data logging: 
   1. [x] Cloud 
   2. [ ] LCD screen.
4. [x] [Debug]3D-print plates.
5. [x] Camera.
6. [x] Data visualization on the 2nd Pi
   1. [x] real-time images, sensor data
   2. [ ] remote control.
7. [x] Chamber assembly, circuit position into the chamber, light and camera ready.

## Meetings

### 9.7.21

**Aims:**

1. Implement fans, pump, humidifier. Position sensors.
2. Test cooling, temperature.

**Minutes:**

1. Implemented fans, pump, camera and sensors. Humidifier still not working.
2. Check out Pictures/Box/Version2/20210709 for updates.

**TODO:**

1. Adjust light
2. Order a 24v DC supply; Adjust camera position; print plate; Start another trial.
3. Adjust python code: Separate scripts.

### 17.6.21

Install light and other device on the chamber. Simplify structure.

Todo:

1. Need to change Relay program (Position; Always on for the top fan)
2. Implement fan, pump and sensor in the next week.

### 3.6.2021

**Aims:**

0. [x] Plot condition data and combine images into a video.
2. [x] Discuss achievement and problems in the first trial, summaries a .md to Trial folder.
	1. Features achieved 
	2. [x] Network connection problems -> split into two codes
	3. [x] Drain: See below
3. [x] Temperature calibration
4. [x] Cooling.
5. [x] Humidity control.
6. [x] Light.
7. [x] Irrigation:
   1. [ ] Intervals: 60h
   2. [ ] watering time: 30->15s
   3. [ ] How to drain remaining water? -> Hole at the bottom
8. [x] Visualisation kit
9. [ ] Next step plans (June):
	4. Controls
	5. modification to box
	6. LCD screen.
	7. Plate 2.0
	8. Irrigation

**Minutes:**

1. To summarise features and problems in the first trial.
2. [ ] Separate Rpi program into 2 python scripts: local logging and upload:
   1. [ ] two ssh sessions
   2. [ ] two .py
3. Cooling:
   1. Fan at the light
   2. Make two holes on the sides of the box, one for air in and another one for air out (with the help with a fan)
4. Irrigation:
   1. Drain a series of holes, with different sizes, at the bottom of the box and test the optimal size
   2. A tray under the lunch box to store extra water, make a holder (Tokenm) to hold the lunch on top of the tray.
   3. With the above, optimise irrigation intervals and duration.
   4. Add a manual control to pump
5. Temperature measurements: don't have to worry so much.
6. :sparkles:Make a portable visualisation kit.
7. Assemble a circuit to show BME680 and NTC values.

To buy:

1. Another fan
2. SD card
3. Cooler
4. Rpi and screen and card and case
5. Thermometer
6. Humidifier
7. Timer switch
8. Relay

### 17.4.2021

Aim:

- Assemble the chamber
- Temperature control, air circulation: fan, relay, heater.
- LCD screen for visualisation.
- [After] Order more hardware, especially light source.
- [After] Print the plate.

Minutes:

- Relay: able to drive fan. 
- But heater is not working.
- Water pump is running: i.e. water every 2 days, 30s each time. #TODO ZD needs to add serial-write to Main.py on Rpi.

## Time table

### Past

| Task Level | 16-22 Nov        | 23-29 Nov                        | 30-06 Dec        |
| ---------- | ---------------- | -------------------------------- | ---------------- |
| Primary    | Github work flow | Look for people and setup design | Application ddl! |

### On-going

| Task Level | Primary                                         | Secondary | Minor |
| ---------- | ----------------------------------------------- | --------- | ----- |
| March      | Sensors                                         | Controls  | ??    |
| Apr        | Growth condition control (Temp,Hum,Light,Water) | ??        | ??    |
| May        | Environment control                      | Light,LCD,remote controls        | ??    |

## April report

Prototype:

1. Chamber assembly
2. Sensors and environment controls
3. Webserver
4. Update Hackstor.

## Application (Done)

Things to prepare and decide:
Che wrote:

- Plan for the project: for the application use and project management.
- Learning from other projects: ongoing.
- Coding method: adurino IDE or XOD or Others.
- Chamber Dimension: What size should it be?
- Sensors: a draft plan like how many sensors? where to put them?
- Actuators: Lights---what wavelenghth?; Water Pump; Robotic Arms---What function we want to achieve with them.
- Flow Chart: Basic logic to link sensors and actuators. To illustrate how things work.

## To learn

Last update: 18.3.21

- [x] Arduino-Pi communication (UART)
- [x] XOD
- [ ] electromechanical relay
- [ ] Voltage divider

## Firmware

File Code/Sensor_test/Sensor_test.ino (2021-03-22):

#include <Wire.h>
#include <SoftwareSerial.h>
#include "RichUNOLM75.h"

// constants won't change. Used here to set a pin number:
const int NTC_Pin = A0;// the number of the NTC(temperature sensor) analog pin.
const int Water_level = A1; // the number of the waterlevel analog pin

LM75 temper;  // initialize an LM75 object "temper" for temperature


void setup() {
  
  Serial.begin(9600);
  Wire.begin();//you should run this function first, so that I2C device can use the I2C bus
  delay(1000);//
}

void loop() {
  // put your main code here, to run repeatedly:
  

  float Temp_LM75_built_in;
  float Temp_NTC_read;
  float Water_level;
  Temp_LM75_built_in = temper.getTemperatue();//get temperature
  Temp_NTC_read = read_ntc_sensor_temp();
  Water_level=read_water_sensro_level();
  
  Serial.print("Temp(LM75 Arduino Built in) "); 
  Serial.print(Temp_LM75_built_in);
  Serial.println(" *C");
  Serial.println("\n");
  Serial.print("Temp(NTC)"); 
  Serial.println(Temp_NTC_read);
  Serial.println(" *C");

  Serial.print("Water Height"); 
  Serial.println(Water_level);
  Serial.println(" mm");
  
  
  
}



float read_ntc_sensor_temp(){
  float Temp_NTC_sensor=0.0; // the temperature reading from the NTC sensore
  int R0=10000;
  int B_parameter=3950;
  int T0=25;
  
  int NUMSAMPLES=5;
  int samples[NUMSAMPLES];
  float average;
  uint8_t i;
  
  // take N samples in a row, with a slight delay
  for (i=0; i< NUMSAMPLES; i++) {
   samples[i] = analogRead(NTC_Pin);
   delay(10);
  }
  // average all the samples out
  average = 0;
  for (i=0; i< NUMSAMPLES; i++) {
     average += samples[i];
  }
  average /= NUMSAMPLES;

  
  // convert the value to resistance
  average = 1023 / average - 1;
  average = R0 / average;
  
  float steinhart;
  steinhart = average / R0;     // (R/Ro)
  steinhart = log(steinhart);                  // ln(R/Ro)
  steinhart /= B_parameter;                   // 1/B * ln(R/Ro)
  steinhart += 1.0 / (T0 + 273.15); // + (1/To)
  steinhart = 1.0 / steinhart;                 // Invert
  steinhart -= 273.15;                         // convert absolute temp to C
  
  return steinhart;
}

float read_water_sensro_level(){
  int NUMSAMPLES=20;
  int samples[NUMSAMPLES];
  float average;
  uint8_t i;
  
  // take N samples in a row, with a slight delay
  for (i=0; i< NUMSAMPLES; i++) {
   samples[i] = analogRead(Water_level);
   delay(10);
  }
  // average all the samples out
  average = 0;
  for (i=0; i< NUMSAMPLES; i++) {
     average += samples[i];
  }
  average /= NUMSAMPLES;

  average /= 1023.;

  float water_height;

  water_height = 24.0*(1.0-average);
  
  return water_height;

}

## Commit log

2020-11-28 Create Biomaker2020-applicationform (gargravarr's conflicted copy 2020-11-25).docx
    Weiming wirte the section for the goal of the hardware design and plan for implementing the project.
2021-01-06 shopping list
    [Expense.xlsx]
2021-01-12 Create Arduino libraries for Rich UNO R3.rar
2021-01-12 Libraries for the sensors on Arduino board and xod sensors
2021-03-22 integrated sensor control file
2021-04-01 add webcam-ZD
    [CHEP_bed_level_print.stl, HSB2_Lid.stl, Head.stl, Hilt.stl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]
2021-04-06 enable google drive
    [calibration.csv]
2021-04-17 Arduino_V2 with relay
2021-04-18 add water function to Main-2.py
    [Picam-front.stl, picam-adapter.stl, picam-back.stl, tripod-base.stl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]
2021-04-27 26.4.21 order
    [24-well-plate.stl, Expense.xlsx, cali.xlsx]
2021-05-12 1. Main-2.2.py: update water intervals and time format in log files. 2. Add Trials without video
    [Expense.xlsx, Log.csv, Temp.xlsx, cali.xlsx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]
2021-06-04 27.4 trial and 3.6 meeting
    [Temp.xlsx, Temp_Calibration.xlsx]
2021-06-21 20210621 meeting and purchase
    [24-well-plate.stl, 24-well-plate_1.0.stl, 24-well-plate_2.0.stl, CHEP_bed_level_print.stl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]
